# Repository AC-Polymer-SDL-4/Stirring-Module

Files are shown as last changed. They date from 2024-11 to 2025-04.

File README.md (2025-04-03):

# Magnetic Stirring Module
 

https://github.com/user-attachments/assets/13f20be7-cdd6-449a-9a6a-96b7d4ccc78b

# Overview
Magnetic stirring is a commonly used method for mixing reagents in chemistry experiments. Through a magnetic field in the stirrer, a stir bar spins quickly to mix components in a flask/vial, creating a uniform mixture and increasing the rate of reactions. This repository contains instructions / materials / code for creating a low-cost stirring module which is programmable and compatible with the Opentrons liquid handler deck slots, so it can be incorporated into automated workflows in self-driving labs (SDLs). 

### Authors
Monique Ngan, Lab Technician \
Owen Alfred Melville, Staff Scientist\
*The 3D design was inspired by SDL 5 \
[Acceleration Consortium](https://acceleration.utoronto.ca/)

## Summary of Steps
1. Order the required parts 
2. 3D Print the case
3. Assemble the electronic components
4. Run code to operate the stirring module

## Tools Required for this Project
- [Soldering Iron](https://www.amazon.ca/Weller-Soldering-Station-WLACCBSH-02-Silicone/dp/B08MC4HVTR?th=1)
- [Heat Gun](https://www.amazon.ca/Mini-Heat-Shrink-Gun-Dual-Temp-dp-B09TYM45BH/dp/B09TYM45BH/ref=dp_ob_title_hi)
- [Wire cutters](https://www.amazon.ca/BOOSDEN-Crafting-Spring-Loaded-Plastics-Clippers/dp/B08ZCHYGN7/?th=1)
- [3D printer](https://ca.store.bambulab.com/products/p1s?srsltid=AfmBOorLX7Ki2ZaYaFx6AWRBcr8wJq_0mTlmHkm-IWXz0sfFRXeNtMNX)

## Required skills
- Soldering
- Basic Python Coding

# Step 1: Order Required Parts
These are the materials required for the current design of the stirring module which holds 6 vials. Note prices may vary over time.

| Item | Supplier | Part Number | Number | Cost (CAD) | Total Cost (CAD) |
| ---- | ----| ----| ----| ----| ----|
| [Raspberry Pi Pico](https://www.pishop.ca/product/raspberry-pi-pico-wh-pre-soldered-headers/) | PiShop | 402-1 | 1 | 9.80 | 9.80 |
| [Raspberry Pi Grove Shield](https://www.digikey.ca/en/products/detail/seeed-technology-co-ltd/103100142/13688265?s=N4IgTCBcDaIIwFYCcB2AtHADAZi5uALGGgHIAiIAugL5A) | DigiKey | 1597-103100142-ND | 1 | 6.32 | 6.32 |
| [25mm x 25mm Square Fan](https://www.digikey.ca/en/products/detail/sunon-fans/MF25100V1-1000U-A99/7805269) | DigiKey | 259-1830-ND | 6 | 14.71 | 88.26 |
| [Barrel Power Connector](https://www.digikey.ca/en/products/detail/same-sky-formerly-cui-devices/PJ-102AH/408448) | DigiKey | CP-102AH-ND | 1 | 1.14 | 1.14 |
| [5V Barrel Power Supply](https://www.digikey.ca/en/products/detail/tri-mag-llc/L6R06H-050/7682614) | DigiKey | 364-1251-ND | 1 | 10.15 | 10.15 |
| [NPN Transistor](https://www.digikey.ca/en/products/detail/nexperia-usa-inc/PZT2222A-115/1158011?s=N4IgTCBcDaIIwHYwILQBYwFYwrigBAHIAiIAugL5A) | DigiKey | 1727-4252-1-ND | 1 | 0.80 | 0.80 |
| [USB A to Micro B Cable](https://www.digikey.com/en/products/detail/cvilux-usa/DH-20M50056/13177301) | DigiKey | DH-20M50056 | 1 | 3.33 | 3.33 |
| [50 V Diode](https://www.digikey.ca/en/products/detail/diotec-semiconductor/1N4001/13164614) | DigiKey |	4878-1N4001CT-ND | 1 | 0.15 | 0.15 |
| Total Cost (CAD)| |  |  | | **119.95** |

### Materials Required - Kits
These materials come in kits, so you may not need them if you already have similar materials. They can be used for other projects as well.
| Item | Supplier | Cost (CAD) | Total Cost (CAD) |
| ---- | ----| ----| ----|
| [PCB Boards](https://www.amazon.ca/BOJACK-6-Prototype-Soldering-Compatible-Arduino/dp/B091PZQ4W7/) | Amazon Canada | 21.99 | 21.99 |
| [Metal Magnets](https://www.amazon.ca/Magnets-Refrigertor-Whiteboard-Durable-Multi-Use/dp/B07BJFD6FL/?th=1) | Amazon Canada | 9.99 | 9.99 |
| [Resistors](https://www.amazon.ca/Resistor-Assorted-Resistors-Assortment-Experiments/dp/B07L851T3V/?th=1) | Amazon Canada | 16.99 | 16.99 |
| [Solder Seal Connectors](https://www.amazon.ca/Kuject-Connectors-Waterproof-Electrical-Automotive/dp/B073RMRCC3/?th=1) | Amazon Canada | 17.99 | 17.99 |
| Total Cost (CAD) |  |  | **66.96** |

### Generic Materials Required
- Solder
- Wires (at least Red & Black)
- Filament for 3D Printing ([PLA](https://ca.store.bambulab.com/products/pla-basic-filament?gad_source=1&gclid=Cj0KCQjwpP63BhDYARIsAOQkATYc5jM-nciSOOw8pbxHA_WIkh3n5OJYfMMvQm4q8-BjsxyQY5-RIlQaAhdqEALw_wcB), [PETG](https://ca.store.bambulab.com/collections/petg/products/petg-hf))

## Photo of Materials


# Step 2: 3D Print the stirring module casing and electronics casing.
In this repo, you can find `.stl` which are 3D printing files for the casing of the stirring module (designed for electrochemical cell vials with a 28mm diameter) and the _optional_ electronics case which holds and organizes the Raspberry Pi (RPi) & PCB.

`Stirring_Module.f3d` is an editable 3D Printing File containing both the lid and base, so the module can be redesigned to fit your needs.

| File Name | Purpose | Filament | Printing Considerations |
| ---- | ----| ----| ----|
| Stirring Module Base.stl | Holds the fans used for stirring | PLA | Print with normal supports.|
| Stirring Module Lid.stl | Holds the vials on top of fans | PLA | Print with the cylinders for the vials facing downwards, with normal supports.|
|Electronics Casing/Pico Holder_MainBody v2.stl| Holds RPi Grove Shield & RPi | PETG | N/A |
|Electronics Casing/Pico Holder_Main_Lid v4.stl| Lid for the Main Component | PETG | N/A |
|Electronics Casing/Pico Holder_Port_Door_Back.stl| Slides into the back of the PCB holding component | PETG| N/A |
|Electronics Casing/Pico Holder_Port_Door_Stirring_Module v2.stl| Slides into the front of the PCB holding component | PETG| Orient with side saying "PORT" facing up |
|Electronics Casing/Pico Holder_Port_Modular v11.stl| Holds the PCB | PETG| N/A|
|Electronics Casing/Pico_Aux_Lid_Snap.stl| Snaps into the top of PCB holding component | PETG| N/A|

# Step 3: Assemble Components
## 3a: Assemble the PCB Board
### Parts Required
- PCB board from Kit (60x40 mm)
- Wires 
- 1x 1000 Ohm resistor
- 1x 5.6 Ohm resistor
- 1x 390 Ohm resistor
- 1x NPN Transistor
- 1x 50V diode
- 1x Power Barrel Connector
- 2x Heat Shrink Connector

### Circuit Diagram
stirring_module_circuit\
_(an image of the soldered PCB is attached below)_

### Soldering Steps
The following instructions will give a written description of the circuit diagram. If you are familiar with electronics, feel free to just solder the circuit diagram. 

1. Mount the barrel connector in the top left corner of the PCB and solder in a 1000 Ohm resistor between the power and ground sides. This creates a power port, where the pin at the back of the barrel connector is your +5V pin, and the pin closer to the opening is the ground (see below).

   
2. The RPi ground pin wire can be a bare wire or a wire with an open pin. Solder in one end of the wire in series between the ground of the barrel connector and the 1K Ohm resistor (See diagram). The other end will be connected to the RPi Grove Shield in a later step.

3. For the NPN transistor, the drawing below shows the schematic (with the trapezoidal piece that protrudes facing towards you). Pin 1 (base) goes to the 390 Ohm resistor and RPi GPIO pin.  Pin 2 (collector) goes to the ground terminal of the fans and Pin 3 (emitter) goes to the ground of the power supply.\
transistor numbering

4. At pin 1, solder a 390 Ohm resistor and one end of the GPIO pin wire (bare or with open pin), like the ground pin wire.
   
6. At pin 2, solder in one end of a black wire. This will be connected to the ground wires of the fan. Repeat the same for a red wire that is connected to a 5.6 Ohm resistor (see diagram).
   
8. Both the fan wires will be connected to a diode. Orient the diode so the silver bar (which indiciates the cathode) points towards the +5V terminal of the fan (the red wire). The diode is used to protect the circuit from the reverse flow of voltage after the fan is turned off, as rotational motors create a magnetic and energetic field which can flow in the opposite direction of the current, damaging the circuit. This way, it will flow back into the fan, using up the energy.

## 3b: Connecting PCB to Fans
1. Place the fans into the square slots in the base piece of the casing. Thread the wires through the hole at the bottom of each slot and collect the wires of the fans in the row at one end of the case.
2. Combine all the black wires (ground) together by twisting the exposed wires together securely. You should have the same number of black wires combined as the number of fans used. Repeat this step for the red wires.
3. Use a heat shrink connector to solder together the combined black wires with the "Fans (Black)(-)" wire from the PCB. Repeat for the red wire and the "Fans (Red)(+)" wire.

## 3c: Assemble PCB & Raspberry Pi
The last step to setting up is connecting the GPIO wires to the Raspberry Pi. The electronic casing (optional) can be printed and used to organize the wires in the project. Slide the side module in with the central square unit.
1. Attach the Raspberry Pi to the Grove Shield. Optionally, place the grove shield and PCB into the square unit and slide on the side unit of the electronic casing.
2. Connect the RPi GPIO Pin 0 wire to the "GP0" slot on the RPi Grove shield. If using the electronic casing, thread the wire through one of the honeycombs in the side panel.
3. Connect the RPi Ground Pin wire to any slot that says "GND" on the RPi Grove shield.

#### Image of Soldered Circuit + RPi


## 3d: Assemble Electronics Casing (Optional)
Finally, insert the side panels into the side module and put on the lids to complete the assembly of the electronics.

# Step 4:  Operating the Stirring Module
1. Download Visual Studio Code (VS Code) and Python.
2. Download the MicroPico Extension in VS Code, which will be used to communicate with the RPi.
3. Plug in the micro USB-B end of the cable into the RPi and the USB-A end into your computer, while pressing the BOOTSEL button on the RPi. This should open a file directory for the RPi on your computer.
4. **Flash the RPi** by downloading the [UF2 file for the RPi Pico W](https://www.raspberrypi.com/documentation/microcontrollers/micropython.html) and transferring the file into the RPi's directory. The file directory should disappear from your files explorer. Unplug and replug the RPi to your computer.
5. Download `stirring_module.py` and open it in VS Code. Feel free to edit this script to accomodate for different uses, for example for changing the stir speed and duration. 

This program contains methods for operating the fan, which are described below and also documented in comments within the script. These methods are called in a try-escape block (to be uncommented out in the code) where the program can be stopped by pressing `ctrl+c` on the keyboard. 
- `initialize_fans()`: This function initializes fans in preparation for stirring.
- `stir_for_duration(power, duration)`: commands the fans to stir at a given power (1-100) which is controlled through pwm signals, for a designated amount of time in _minutes_.
- `stir(power)`: commands the fans to stir at the given power until the stop() command is run
- `stop()`: stops and deinitializes the fans
- `initialize_and_stir(power, duration)`: initializes and stirs for the specified duration of time
- `controller_stir(power)`: to be used in a controller class to command the fans to stir at a certain power
- `controller_stop()`: to be used in a controller class to stop stirring

- The on-board LED is also turned on while stirring is on, and turned off when stirring is stopped.

6. To run the file, right click in the editor and select **"Upload file to Pico"** and **"Run File on Pico"** afterwards. Be sure to **uncomment** the try-escape block to run the methods described.

7. Optionally, the module can be run without using the MicroPico REPL terminal, using the Python subpackage module. Download and run `stirring_module_controller.py`, where the fans can be commanded to start stirring (`start_stirring(power)`), stop stirring (`stop_stirring()`) and stir for a specified duration (`stir_for_duration(power,duration)`).
      -  Note that `stirring_module.py` needs to be uploaded to the RPi and the Pico needs to be disconnected in the MicroPico terminal. As well, the **COM number** (in line 15 of stirring_module_controller.py) needs to be changed to the COM number your module is connected to. You can check this through Windows > Device manager > Ports.

*🎉🎉Congratulations you are all set for using the stirring module!*

## Tested Power Values for Solutions of Various Viscosities
- Minimum power: **45** for all fans to turn on. Lower than this, only some fans will operate.
- Maximum power: **92**. Higher than this, the fans turn too quickly and the whole module starts to shake.

| Solution (listed in increasing viscosity) | Micro Stir Bar | Larger Stir Bar (514) |
| ---- | ----| ----|
| Acetone | 45-75 | 60-75 (80 starts to bounce) |
| Water  | 45-70 | 60-90 |
| 0.1% PEG in water  | 45-80 | 50-80 |
| 10% PEG in water  | 45-85 | 60-85 |
| 25% PEG in water  | 70-92 (for all speeds - mainly vibrates and doesn't stir well) | 70-80 |
| 50% PEG in water | Not possible | Not possible (70 moves very slowly, still only vibrating at 92) |

## Trouble Shooting Common Errors
**Error 1**: Trouble Connecting to RPi (when using the MicroPico Extension in VSCode)
Screenshot of Micropico Connection Error
or a `error running on raw repl` \
=> Restart VSCode. If this does not help, restart your computer.\
Other potential solutions: uninstall / reinstall MicroPico extension & check if the RPi is connected (Windows > Device Manager > Ports, To see if RPi is connected via USB) 

**Error 2**: COM in use (when using subprocess to operate RPi) \
Ensure the RPi is disconnected in the MicroPico REPL terminal, as both can not be connected at the same time.

**Error 3**: mpremote module not found \
Try installing and reinstalling the mpremote package using pip install.

**Error 4**: on-board LED not turning on \
Back up all files on the RPi and disconnect from your computer. NOTE: Bootsel mode will remove all files on the microcontroller. Put the RPi in bootsel mode (by pressing the bootsel button) and reconnect it to your computer while the button is pressed. Reinstall the RPi [firmware](https://www.raspberrypi.com/documentation/microcontrollers/micropython.html).

## Current Limitations & Future Work
- Currently, the individual fans are spinning at slightly different speeds which is important to note for lower stir speeds as some fans may stop stirring as it does not have enough power. Future prototypes should work on improving electrical connections to the fans, as this is the suspected reason for this issue.
- Orchestration with the Opentrons / other liquid dispensers

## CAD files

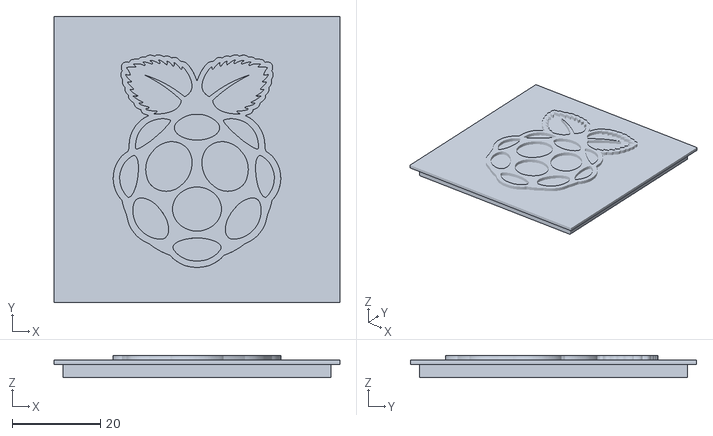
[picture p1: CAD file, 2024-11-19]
Electronics Casing/Pico Holder_Main_Lid v4.stl
65.0 x 65.0 x 5.00

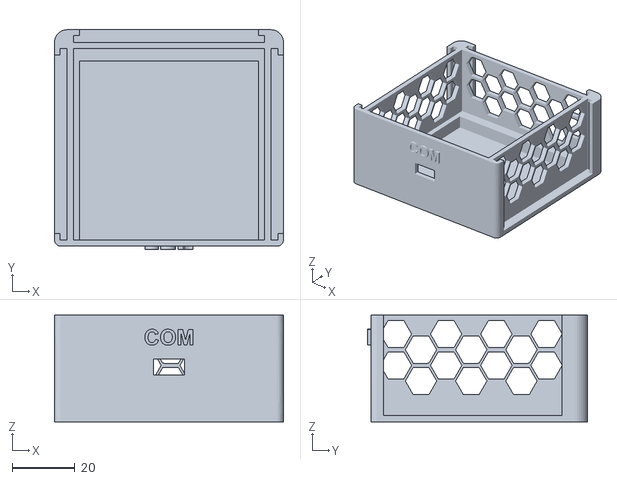
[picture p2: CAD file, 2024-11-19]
Electronics Casing/Pico Holder_MainBody v2.stl
73.0 x 70.0 x 34.0

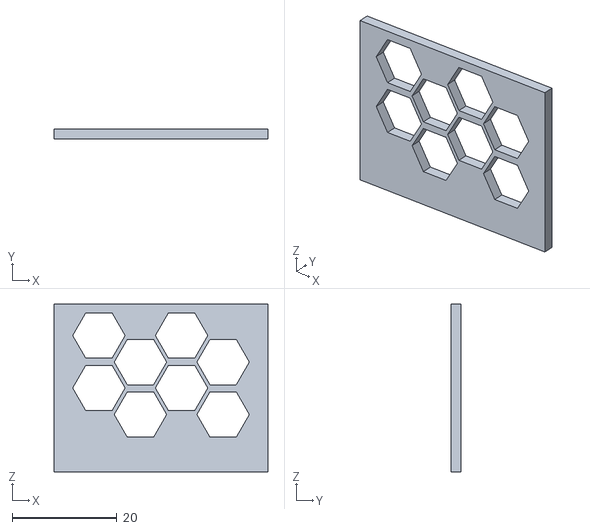
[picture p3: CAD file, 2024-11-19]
Electronics Casing/Pico Holder_Port_Door_Back.stl
40.8 x 2.00 x 32.0

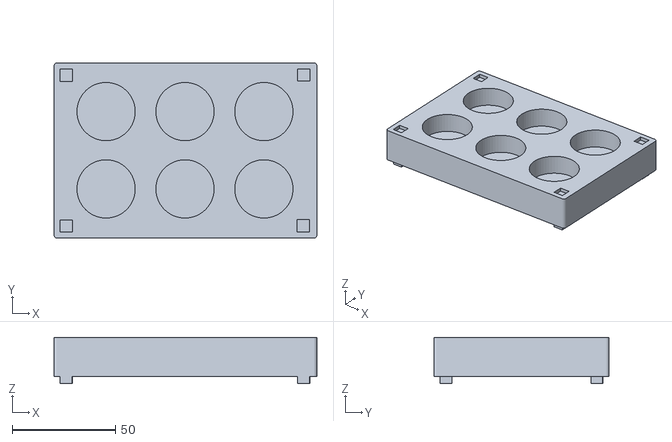
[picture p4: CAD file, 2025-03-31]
Stirring Module Lid.stl
127.5 x 85.0 x 22.5

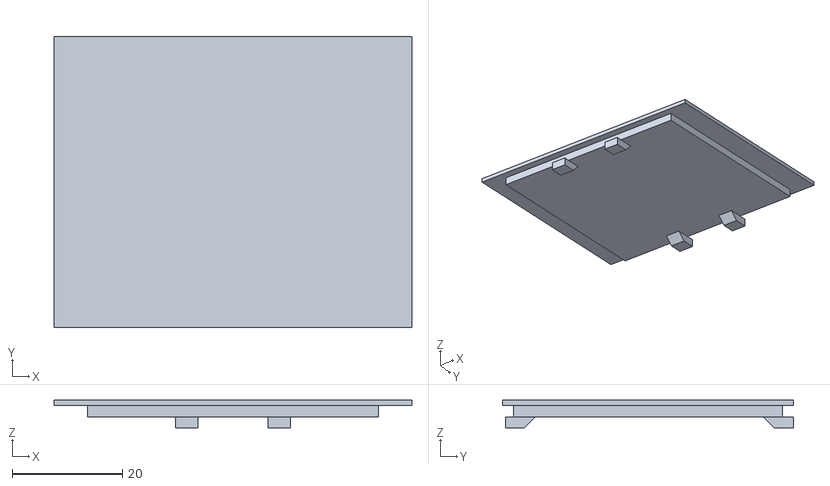
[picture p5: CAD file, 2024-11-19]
Electronics Casing/Pico_Aux_Lid_Snap.stl
65.0 x 52.8 x 5.00

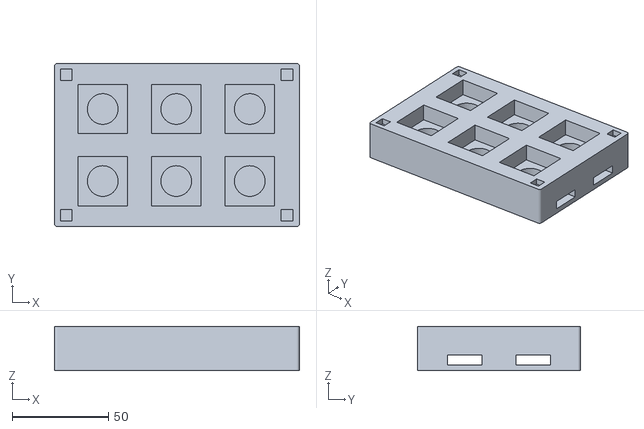
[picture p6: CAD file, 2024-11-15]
Stirring Module Base.stl
127.5 x 85.0 x 23.0

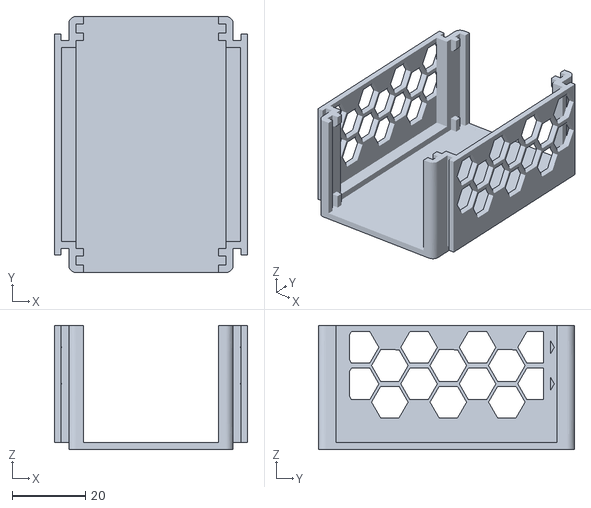
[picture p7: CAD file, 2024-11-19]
Electronics Casing/Pico Holder_Port_Modular v11.stl
52.8 x 70.1 x 34.0

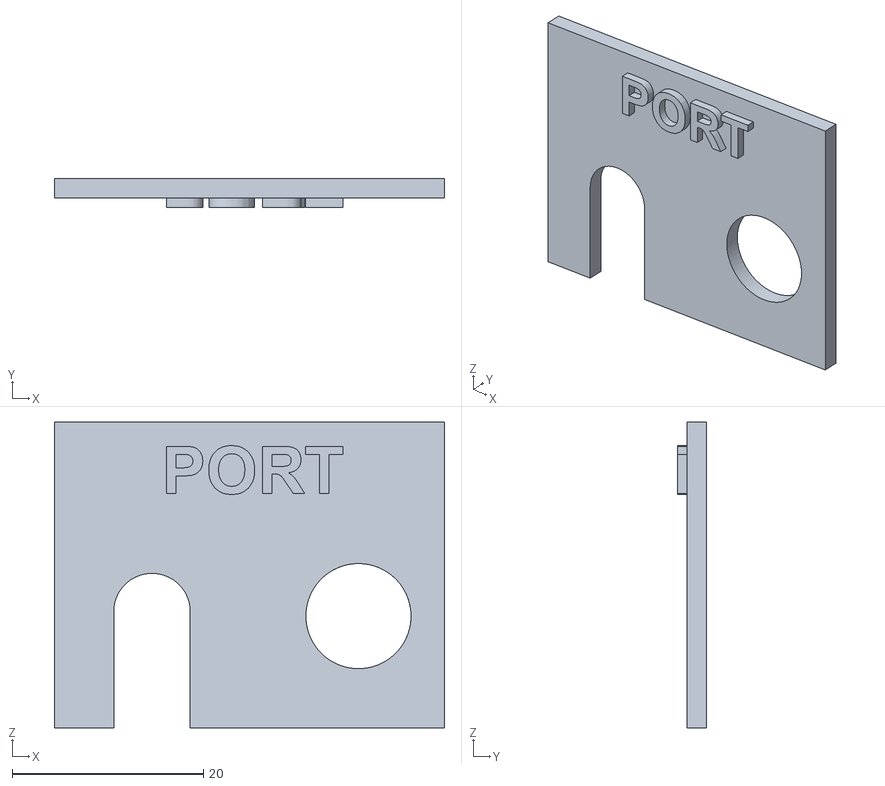
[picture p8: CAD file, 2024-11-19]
Electronics Casing/Pico Holder_Port_Door_Stirring_Module v2.stl
40.8 x 3.00 x 32.0

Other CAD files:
Stirring Module V2.f3d

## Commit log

2024-11-15 Added 3D Printing Files for module
    [Stirring Module Base.stl, Stirring Module Lid.stl]
2024-11-19 Added electronics casing 3D printing files
    [Pico Holder_MainBody v2.stl, Pico Holder_Main_Lid v4.stl, Pico Holder_Port_Door_Back.stl, Pico Holder_Port_Door_Stirring_Module v2.stl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]
2024-12-13 Added fusion file for editing
    [Stirring_Module.f3d]
2025-02-26 Major changes: turn on, turn off and led indication
2025-03-03 Updated LED status indication
2025-03-31 Updated alignment
    [Stirring Module Lid.stl]
